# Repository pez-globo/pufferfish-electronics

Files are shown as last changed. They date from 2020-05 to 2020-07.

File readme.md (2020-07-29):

# pufferfish-electronics

Electronic hardware board layout files for the Pufferfish ventilator.

This folder contains the [KiCad](https://kicad-pcb.org/) design files for the Pufferfish ventilator.

To review the hardware files, start by opening the project file `Pufferfish.pro` with KiCad. From there, schematics, boards, and library parts can be viewed.

`Pufferfish.sch` and `Pufferfish.kicad_pcb` are dummy files, kept to aid in managing project resources (eg. footprint and schematic library settings).

The files `sym-lib-table` and `fp-lib-table` define the paths for local part libraries. 
  * these should point to `/library/symbols/` and `/library/footprints/` for symbols and footprints, respectively. 
  * this only applies to projects containing in this folder and not subfolders below it. 
  * for each design project, its own `sym-lib-table` and `fp-lib-table` files were added pointing to: `${KIPRJMOD}/../../library/symbols/Pufferfish.lib` and `${KIPRJMOD}/../../library/footprints/Pufferfish.pretty, respectively`
  * if this relative linking fails, an alternative way to share these library parts amongst each project is to add them to KiCad's global library path (open any project or schematic or pcb, add the appropriate library directories by going to "Preferences/Manage <Footprint/Symbol> Library", and when prompted choose global).

The file `Pufferfish.kicad_wks` contains the template schematic page layout for this project.

Copyright 2020, the Pez Globo team and the Pufferfish project contributors

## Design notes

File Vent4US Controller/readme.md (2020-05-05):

This folder contains the EasyCAD design files for the Vent4US control board, which was forked from the [Octopi](https://octopi.squarespace.com/) project: https://github.com/ethanjli/octopi-driver-board

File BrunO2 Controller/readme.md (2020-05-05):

This folder contains the [Eagle](https://www.autodesk.com/products/eagle/overview) design files for the [BrunO2](https://sites.brown.edu/bruno2/) Control Board v1, as designed by Marc Powell in April of 2020 at Brown Univeristy.

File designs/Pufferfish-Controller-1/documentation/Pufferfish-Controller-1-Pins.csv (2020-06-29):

Board | Name | MCU Pin Name | Board Net | MCU Pin Function | Type | Domain | Description
control | CN11_56 | PF9 | SENSE_O2_OUT | ADC3_INP2 | ADC | oxygen sensor | oxygen sensor output
control | CN11_55 | PD1 | MOTOR1_UART | UART4_TX | UART | motor driver | universal asynchronous transmitter for configuring a motor driver
control | CN11_3 | PC12 | MOTOR2_UART | UART5_TX | UART | motor driver | universal asynchronous transmitter for configuring a motor driver
control | CN11_11 | PF7 | MOTOR3_UART | UART7_TX | UART | motor driver | universal asynchronous transmitter for configuring a motor driver
control | CN11_61 | PE1 | MOTOR4_UART | UART8_TX | UART | motor driver | universal asynchronous transmitter for configuring a motor driver
control | CN12_17 | PB6 | CPU_UART_TX | USART1_TX | USART | computer | microcontroller and computer communication channel
control | CN12_33 | PA10 | CPU_UART_RX | USART1_RX | USART | computer | microcontroller and computer communication channel
control | CN12_23 | PA8 | CPU_UART_CLK | USART1_CK | USART | computer | microcontroller and computer communication channel
control | CN12_12 | PA12 | CPU_UART_RTS | USART1_RTS | USART | computer | microcontroller and computer communication channel
control | CN12_14 | PA11 | CPU_UART_CTS | USART1_CTS | USART | computer | microcontroller and computer communication channel
control | CN12_11 | PA5 | SPI1_SCL | SPI1_SCK | SPI | pressure sensor | pressure sensor communication channel
control | CN12_13 | PA6 | SPI1_MISO | SPI1_MISO | SPI | pressure sensor | pressure sensor communication channel
control | CN12_15 | PA7 | SPI1_MOSI | SPI1_MOSI | SPI | pressure sensor | pressure sensor communication channel
control | CN11_32 | PA4 | <no connection> | SPI1_NSS | SPI | pressure sensor | pressure sensor communication channel
control | CN11_17 | PA15 | BUZZ1_EN | TIM2_CH1 | PWM | buzzer | pulse width modulated line for driving the buzzer
control | CN11_62 | PE6 | LED1_EN | Digital I/O | DIO | light indicator | digital line for indicating program status via a light emitting diode
control | CN11_64 | PG15 | LED2_EN | Digital I/O | DIO | light indicator | digital line for indicating program status via a light emitting diode
control | CN11_66 | PG10 | LED3_EN | Digital I/O | DIO | light indicator | digital line for indicating program status via a light emitting diode
control | CN12_67 | PG7 | MOTOR1_EN | Digital I/O | DIO | motor driver | digital line for enabling a motor driver
control | CN12_43 | PD12 | MOTOR1_DIR | Digital I/O | DIO | motor driver | digital line for controlling motor direction
control | CN12_45 | PD11 | MOTOR1_STEP | Digital I/O | DIO | motor driver | digital line for controlling motor steps
control | CN12_47 | PE10 | MOTOR2_EN | Digital I/O | DIO | motor driver | digital line for enabling a motor driver
control | CN12_49 | PE12 | MOTOR2_DIR | Digital I/O | DIO | motor driver | digital line for controlling motor direction
control | CN12_51 | PE14 | MOTOR2_STEP | Digital I/O | DIO | motor driver | digital line for controlling motor steps
control | CN12_53 | PE15 | MOTOR3_EN | Digital I/O | DIO | motor driver | digital line for enabling a motor driver
control | CN12_55 | PE13 | MOTOR3_DIR | Digital I/O | DIO | motor driver | digital line for controlling motor direction
control | CN12_57 | PF13 | MOTOR3_STEP | Digital I/O | DIO | motor driver | digital line for controlling motor steps
control | CN12_59 | PF12 | MOTOR4_EN | Digital I/O | DIO | motor driver | digital line for enabling a motor driver
control | CN12_61 | PG14 | MOTOR4_DIR | Digital I/O | DIO | motor driver | digital line for controlling motor direction
control | CN12_65 | PD10 | MOTOR4_STEP | Digital I/O | DIO | motor driver | digital line for controlling motor steps
control | CN12_37 | PA3 | DRIVE1_CH1_EN | TIM2_CH4 | PWM | solenoid driver | digital line for enabling a solenoid driver
control | CN12_31 | PB3 | DRIVE1_CH2_EN | TIM2_CH2 | PWM | solenoid driver | digital line for enabling a solenoid driver
control | CN12_24 | PB1 | DRIVE1_CH3_EN | TIM3_CH4 | PWM | solenoid driver | digital line for enabling a solenoid driver
control | CN12_27 | PB4 | DRIVE1_CH4_EN | TIM3_CH1 | PWM | solenoid driver | digital line for enabling a solenoid driver
control | CN12_29 | PB5 | DRIVE1_CH5_EN | TIM3_CH2 | PWM | solenoid driver | digital line for enabling a solenoid driver
control | CN12_2 | PC8 | DRIVE1_CH6_EN | TIM3_CH3 | PWM | solenoid driver | digital line for enabling a solenoid driver
control | CN11_21 | PB7 | DRIVE1_CH7_EN | TIM4_CH2 | PWM | solenoid driver | digital line for enabling a solenoid driver
control | CN12_46 | PD14 | DRIVE2_CH1_EN | TIM4_CH3 | PWM | solenoid driver | digital line for enabling a solenoid driver
control | CN12_48 | PD15 | DRIVE2_CH2_EN | TIM4_CH4 | PWM | solenoid driver | digital line for enabling a solenoid driver
control | CN11_28 | PA0 | DRIVE2_CH3_EN | TIM5_CH1 | PWM | solenoid driver | digital line for enabling a solenoid driver
control | CN12_4 | PC6 | DRIVE2_CH4_EN | TIM8_CH1 | PWM | solenoid driver | digital line for enabling a solenoid driver
control | CN12_19 | PC7 | DRIVE2_CH5_EN | TIM8_CH2 | PWM | solenoid driver | digital line for enabling a solenoid driver
control | CN12_1 | PC9 | DRIVE2_CH6_EN | TIM8_CH4 | PWM | solenoid driver | digital line for enabling a solenoid driver
control | CN12_26 | PB15 | DRIVE2_CH7_EN | TIM12_CH2 | PWM | solenoid driver | digital line for enabling a solenoid driver
control | CN12_52 | PE9 | SENSE_O2_EN | Digital I/O | DIO | oxygen sensor | digital line for enabling an oxygen sensor
control | CN12_56 | PE11 | PRESS1_EN | Digital I/O | DIO | pressure sensor | digital line for enabling a pressure sensor
control | CN12_58 | PF3 | PRESS2_EN | Digital I/O | DIO | pressure sensor | digital line for enabling a pressure sensor
control | CN12_60 | PF15 | PRESS3_EN | Digital I/O | DIO | pressure sensor | digital line for enabling a pressure sensor
control | CN12_62 | PF11 | PRESS4_EN | Digital I/O | DIO | pressure sensor | digital line for enabling a pressure sensor
control | CN12_64 | PE0 | PRESS5_EN | Digital I/O | DIO | pressure sensor | digital line for enabling a pressure sensor
control | CN12_66 | PG8 | PRESS6_EN | Digital I/O | DIO | pressure sensor | digital line for enabling a pressure sensor
control | CN11_68 | PG13 | PRESSX_EN | Digital I/O | DIO | pressure sensor | digital line for enabling/interrupting a set of I2C pressure sensors
control | CN12_16 | PB12 | <no connection> | I2C2_SMBA | I2C | flow sensor | flow sensor (and oxygen sensor) communication channel
control | CN12_25 | PB10 | I2C1_SCL | I2C2_SCL | I2C | flow sensor | flow sensor and oxygen sensor communication channel
control | CN12_18 | PB11 | I2C1_SDA | I2C2_SDA | I2C | flow sensor | flow sensor and oxygen sensor communication channel
control | CN12_68 | PG5 | I2C1_RESET | Digital I/O | DIO | flow sensor | digital line for resetting I2C multiplexer of flow sensors
control | CN12_3 | PB8 | I2C2_SCL | I2C1_SCL | I2C | pressure sensor | pressure sensor communication channel
control | CN12_5 | PB9 | I2C2_SDA | I2C1_SDA | I2C | pressure sensor | pressure sensor communication channel
control | CN12_70 | PG6 | I2C2_RESET | Digital I/O | DIO | pressure sensor | digital line for resetting I2C multiplexer of pressure sensors
control | CN12_41 | PD13 | I2C3_SDA | I2C4_SDA | I2C | oxygen sensor | oxygen sensor communication channel
control | CN12_50 | PF14 | I2C3_SCL | I2C4_SCL | I2C | oxygen sensor | oxygen sensor communication channel
control | CN12_69 | PG4 | PRESS_VDD_EN | Digital I/O | DIO | pressure sensor | pressure sensor voltage supply enable (allows for software resetting certain pressure sensor devices)
interface | CH7_5 | PB13 | ALARM1_LOW | Digital I/O | DIO | buzzer | set high to turn on low-urgency, regulation-compliant, alarm sound
interface | CH10_2 | PG12 | ALARM1_HIGH | Digital I/O | DIO | buzzer | set high to turn on high-urgency, regulation-compliant, alarm sound
interface | CH11_30 | PA1 | ALARM1_MED | Digital I/O | DIO | buzzer | set high to turn on medium-urgency, regulation-compliant, alarm sound
interface | CN8_6 | PC10 | LEDR_CNTRL | Digital I/O | DIO | light indicator | set high to turn on red LED
interface | CN8_8 | PC11 | LEDB_CNTRL | Digital I/O | DIO | light indicator | set high to turn on blue LED
interface | CN8_10 | PD2 | LEDG_CNTRL | Digital I/O | DIO | light indicator | set high to turn on green LED
interface | CN8_14 | PG2 | SET_ALARM_EN | Digital I/O | DIO | user button | digital push input, high = alarm enabled
interface | CN8_16 | PG3 | SET_LOCK | Digital I/O | DIO | user button | digital push input, high = ventilation lock
interface | CH10_15 | PB2 | SET_PWR_SRC | Digital I/O | DIO | user button | digital rocker input for selecting power source
interface | CH10_25 | PE2 | SET_PWR_ON_OFF | Digital I/O | DIO | user button | digital rocker input for power on/off
interface | CN12_28 | PB14 | ALARM2_CNTRL | TIM12_CH1 | PWM | buzzer | pwm signal that controls piezo buzzer (not regulation compliant)
power | CN11_43 | PD6 | LTC4421-PWR-nDISABLE1 | Digital I/O | DIO | power prioritizer | Channel 1 (primary power source) disable
power | CN11_59 | PG0 | LTC4421-PWR-nCH1 | Digital I/O | DIO | power prioritizer | Indicates if primary power source is currently used as power path
power | CN11_39 | PD4 | LTC4421-PWR-nVALID1 | Digital I/O | DIO | power prioritizer | Indicates valid voltage range for primary power source
power | CN11_45 | PD7 | LTC4421-PWR-nDISABLE2 | Digital I/O | DIO | power prioritizer | Channel 2 (backup battery) disable
power | CN11_51 | PF1 | LTC4421-PWR-nFAULT1 | Digital I/O | DIO | power prioritizer | Fault flag for primary power channel
power | CN11_58 | PG1 | LTC4421-PWR-nCH2 | Digital I/O | DIO | power prioritizer | Indicates if battery backup is currently used as power path
power | CN11_41 | PD5 | LTC4421-PWR-nVALID2 | Digital I/O | DIO | power prioritizer | Indicates valid voltage range for backup power source
power | CN11_53 | PF0 | LTC4421-PWR-nFAULT2 | Digital I/O | DIO | power prioritizer | Fault flag for backup power channel
power | CN11_48 | PE4 | VSYS-5V0-PGOOD | Digital I/O | DIO | regulator | 5V Buck PGOOD flag
power | CN11_47 | PE3 | VSYS-3V3-PGOOD | Digital I/O | DIO | regulator | 3.3V Buck PGOOD flag
power | CN11_52 | PF2 | BAT-CHARGE-EN | Digital I/O | DIO | battery | Enables charging path for SLA backup battery
power | CN11_50 | PE5 | BAT-MEAS-EN | Digital I/O | DIO | battery | Enables analog measurement of backup battery
power | CN11_54 | PF8 | BAT-MEAS-ANALOG | ADC3_INP7 | ADC | battery | Analog divider measurement from battery
control | CN12_6 | PC5 | GPIO1 | Digital I/O | DIO | unused | unused general purpose I/O line for off board routing
control | CN12_34 | PC4 | GPIO2 | Digital I/O | DIO | unused | unused general purpose I/O line for off board routing
control | CN12_40 | PE8 | GPIO3 | Digital I/O | DIO | unused | unused general purpose I/O line for off board routing
control | CN12_44 | PE7 | SET_EXTRA | Digital I/O | DIO | unused | unused general purpose I/O line for off board routing

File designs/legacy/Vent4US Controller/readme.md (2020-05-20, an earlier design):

This folder contains the [EasyEDA](https://easyeda.com/) design files for the Vent4US control board, which was forked from the [Octopi](https://octopi.squarespace.com/) project: https://github.com/ethanjli/octopi-driver-board

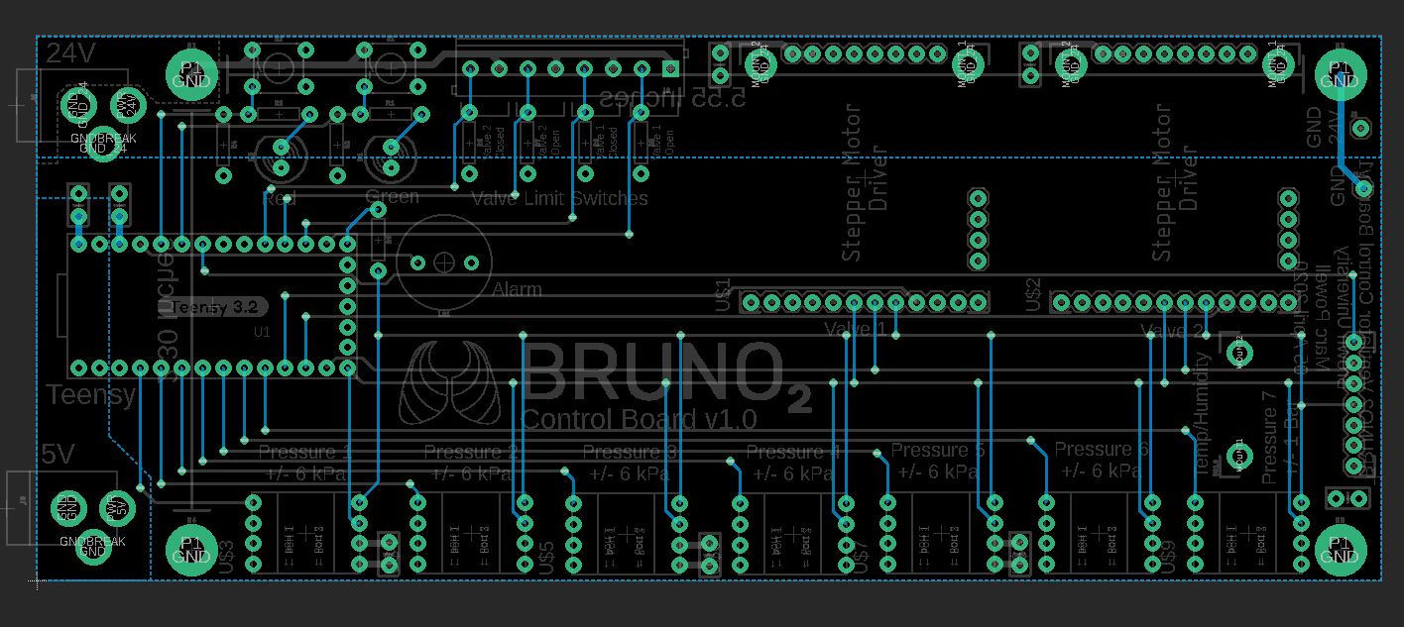
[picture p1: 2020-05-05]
BrunO2 Controller/graphics/Board_Bottom.PNG

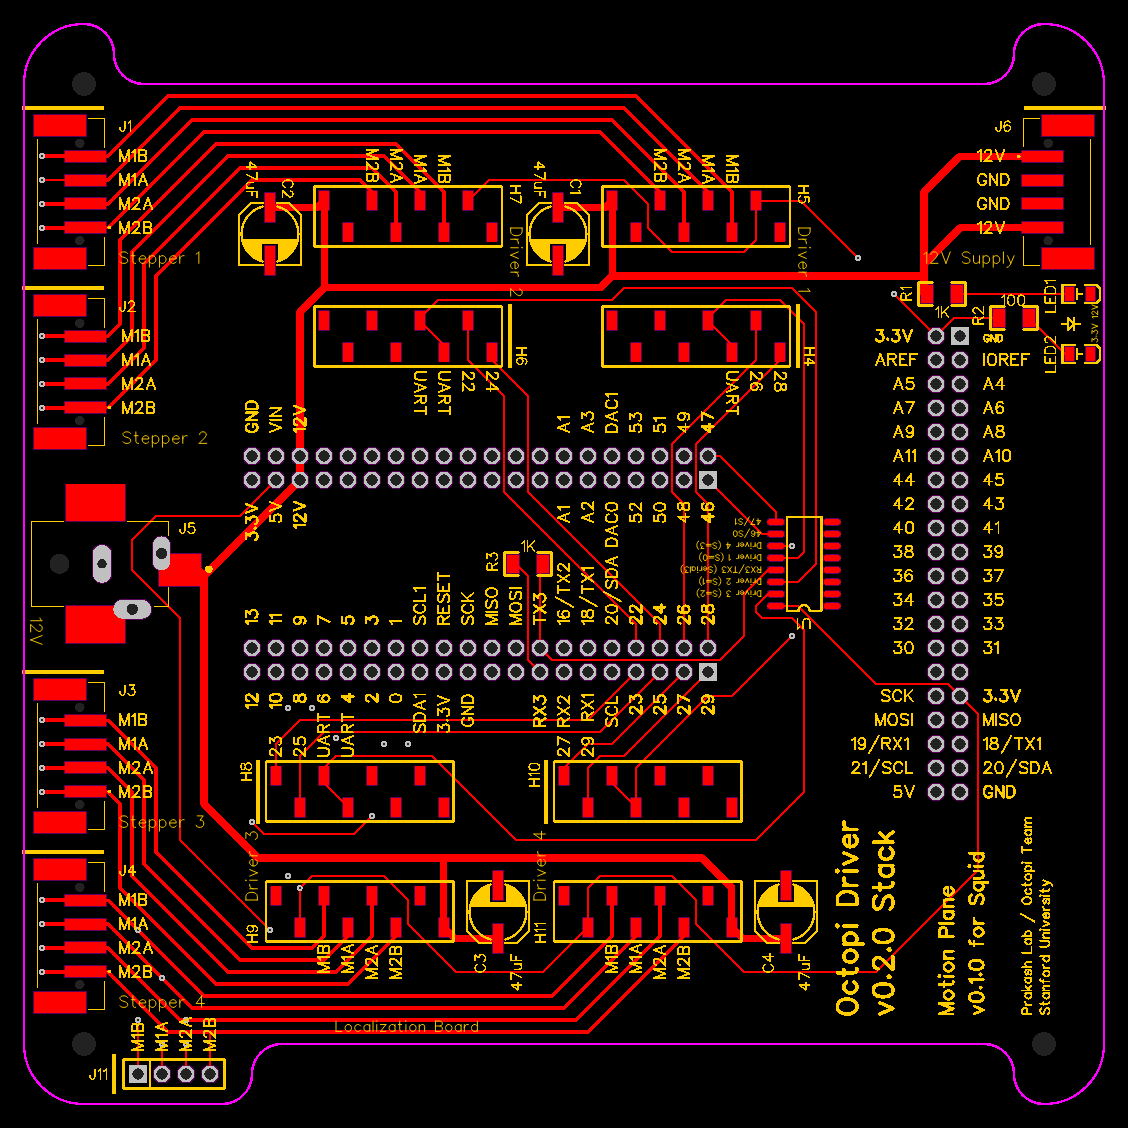
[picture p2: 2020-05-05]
Vent4US Controller/graphics/Layout Top.png

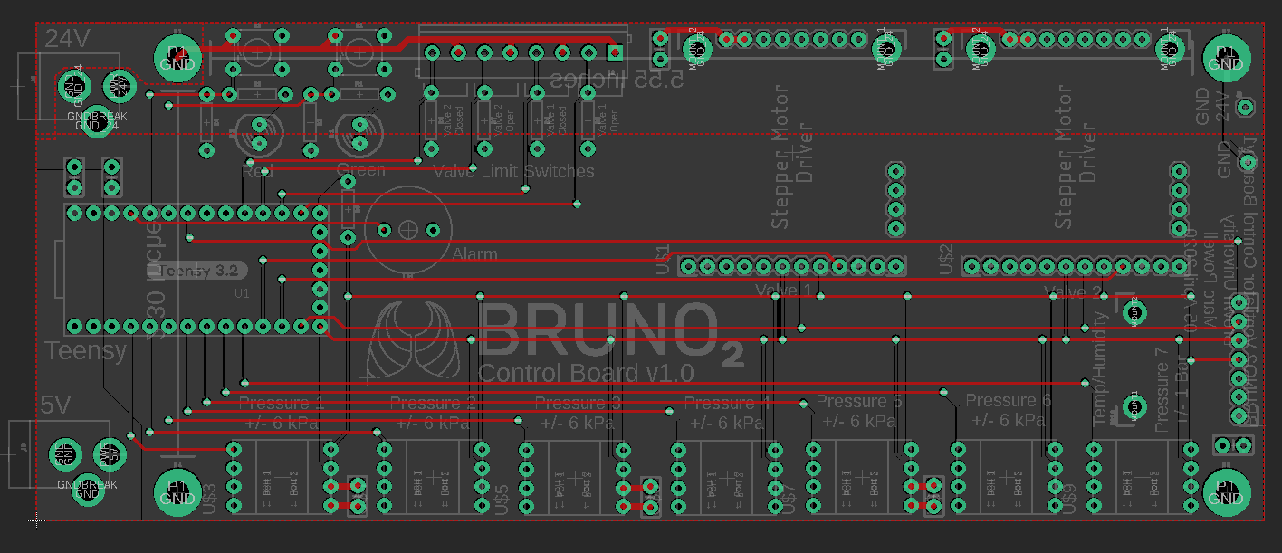
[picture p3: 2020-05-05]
BrunO2 Controller/graphics/Board_Top.PNG

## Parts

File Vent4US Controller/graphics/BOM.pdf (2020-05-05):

BOM for ODS-MPSv0.1.0 | Components

ID

Component

ID | Image Component Name | Mounting Type Manufacturer | Manufacturer Part # | Manufacturer Link | Supplier
Supplier Part # | Supplier Link Supplier Description
ShenZhen OPL MPN Component Notes | Quantity
EasyEDA BOM ID | Designator Notes
1 | 15 | Motion Plane v0.1.0 | Fastener | Seeed Studio

Octopi Team

ODS- MPSv0.1.0 https://github.com/ethanjli/octopi-driver-board/tree/ODS-MPSv0.1.0/Stacked/Motion%20Plane%20for%20Squid Motion Plane v0.1.0 for Squid | 1 N/A
2 | 5
2x20 Female Header, Tall Stacking | PTH

Sullins Connector Solutions

PPPC202LFH
N-M53 RC | https://media.digikey.com/pdf/Data%20Sheets/Sullins%20PDFs/Female_Headers.100_DS.pdf Pololu | 2749 https://www.pololu.com/product/2749
Stackable 0.100″ Female Header with Extra 0.3″ Spacer: 2x20-Pin, Straight | Next version will replace with SMT headers. | 3 | 6 C1,C3,C2

The female side should be on the underside of the board, while the male pins should stick up.

3 | 16
SilentStepStick Stepper Driver Board | Daughter Board Trinamic | TMC2209 | https://www.trinamic.com/support/eval-kits/details/silentstepstick/ Digi-Key
1460-1395- ND | https://www.digikey.com/product-detail/en/trinamic-motion-control-gmbh/TMC2209-SILENTSTEPSTICK/1460-1395-ND/10232488 TMC2209 STEPPER DRIVER BOARD | 4 N/A

Driver 1, Driver 2, Driver 3, Driver 4
Solder the UART/PDN jumper pads on the board first! Then place on the male headers (short ends), confirm correct orientation, and solder.
4 | 17 | 1x8 Female Header | SMT

Sullins Connector Solutions

NPPC081KFX C-RC | https://www.sullinscorp.com/product/?pn=NPPC081KFXC-RC&toggle=in Digi-Key | S5639-ND https://www.digikey.com/product-detail/en/sullins-connector-solutions/NPPC081KFXC-RC/S5639-ND/776098 CONN HDR 8POS 0.1 GOLD SMD | 8 | 8

H4, H5, H6, H7, H8, H9, H10, H11

5 | 9 | 1X8 Male Header | PTH | Pololu | 965 https://www.pololu.com/product/965 Pololu | 965 https://www.pololu.com/product/965 0.100" (2.54 mm) Breakaway Male Header: 1×40-Pin, Straight, Black
Next version will replace with SMT header. Need to break off appropriate length of header. | 8 N/A

H4, H5, H6, H7, H8, H9, H10, H11
Break of appropriate length of header and insert long ends into the female headers.
6 | 18 | 100uF Electrolytic Capacitor | SMT | Nichicon | UCD1E470MC
L1GS | https://www.nichicon.co.jp/english/products/pdfs/e-ucd.pdf (https://www.digikey.com/product-detail/en/nichicon/UCD1E470MCL1GS/493-6385-1-ND/3438899) Digi-Key
| | | | | | 493-6385- 1-ND https://www.digikey.com/product-detail/en/nichicon/UCD1E470MCL1GS/493-6385-1-ND/3438899 CAP ALUM 47UF 20% 25V SMD

UCD1E47
0MCL1GS | 4 | 11
C1,C2,C3, C4 | Confirm correct orientation.
7 | 19 | DC Power Jack | SMT | CUI Devices
PJ-037AH- SMT-TR | https://www.cuidevices.com/product/interconnect/connectors/dc-power-connectors/jacks/pj-037ah-smt-tr Digi-Key

CP- 037AHPJC

T-ND https://www.digikey.com/product-detail/en/cui-devices/PJ-037AH-SMT-TR/CP-037AHPJCT-ND/1530998 CONN PWR JACK 2X5.5MM SOLDER | 1 | 5 J5

Solder the SMT pads first, then solder the PTH pins.

8 | 20 | Green Indicator LED | SMT

Everlight Electronics

17- 21SYGC/S530

-E2/TR8 | http://www.everlight.com/SeriationProduct.aspx?Seq=04c91a6b-2405-e411-8b3b-0002a54e500f (https://www.digikey.com/product-detail/en/everlight-electronics-co-ltd/17-21SYGC-S530-E2-TR8/1080-1500-1-ND/7707772) Digi-Key

1080-1500- 1-ND https://www.digikey.com/product-detail/en/everlight-electronics-co-ltd/17-21SYGC-S530-E2-TR8/1080-1500-1-ND/7707772 LED YELLOW/GREEN CLEAR 0805 SMD

17- 21SYGC/S

530- E2/TR8 | 2 | 12 LED1,LED2 Confirm correct orientation.
9 | 21 | 1K Resistor | SMT | Yageo
RC1206FR- 071KL | https://www.yageo.com/en/Product/Index/rchip/thick_film_general_purpose Digi-Key
311-1.00 KFRCT-ND https://www.digikey.com/product-detail/en/%E5%9E%88-%C3%A1/RC1206FR-071KL/311-1-00KFRCT-ND/731334 RES SMD 1K OHM 1% 1/4W 1206

RC1206JR
-071KL | 2 | 9 R1,R3
10 | 22 | 100 Resistor | SMT | Yageo
RC1206FR- 07100RL | https://www.yageo.com/en/Product/Index/rchip/thick_film_general_purpose Digi-Key
311- 100FRCT- ND | https://www.digikey.com/product-detail/en/%E5%9E%88-%C3%A1/RC1206FR-07100RL/311-100FRCT-ND/731438 RES SMD 100 OHM 1% 1/4W 1206
RC1206JR
-07100RL | 1 | 13 R2
11 | 23 | SP4T Mux/Demux | SMT | Nexperia
74HC4052D, 653 | https://www.nexperia.com/products/analog-logic-ics/i-o-expansion-logic/analog-switches/74HC4052D.html Digi-Key
1727-2808- 1-ND | https://www.digikey.com/product-detail/en/nexperia-usa-inc/74HC4052D-653/1727-2808-1-ND/763388 IC MUX/DEMUX DUAL 4X1 16SOIC

74HC4052 D,653

In a future version, we'll try using the MS1/MS2 UART addressing system instead of a UART mux/demux. | 1 | 10 U1 | Confirm correct orientation.
12 | 24
1x4 Spring Clamp Terminal Block | SMT | Phoenix Contact | 1814650 https://www.phoenixcontact.com/online/portal/us/?uri=pxc-oc-itemdetail:pid=1814650&library=usen&pcck=P-11-01-05&tab=1&selectedCategory=ALL Digi-Key
277-10064- 1-ND | https://www.digikey.com/product-detail/en/phoenix-contact/1814650/277-10064-1-ND/4738862 TERM BLOCK 4POS | 4 | 2 J1,J2,J3,J4
First solder the pads on the side, then solder the SMT pins.
13 | 25
1x6 1.5mm Pitch Right-Angle Header | SMT | JST

S6B-ZR- SM4A-TF(LF)

(SN) | http://www.jst-mfg.com/product/detail_e.php?series=287 (https://www.digikey.com/product-detail/en/jst-sales-america-inc/S6B-ZR-SM4A-TF-LF-SN/455-1610-1-ND/858041) Digi-Key
455-1610- 1-ND | https://www.digikey.com/product-detail/en/jst-sales-america-inc/S6B-ZR-SM4A-TF-LF-SN/455-1610-1-ND/858041 CONN HEADER SMD R/A 6POS 1.5MM | 4 | 1

J7,J8,J9,
J10

First solder the pads on the side, then solder the SMT pins.

14 | 28 | 16 Position 1.5mm Pitch Cable Wiring | JST

A06ZR06ZR2
8H305B | http://www.jst-mfg.com/product/pdf/eng/eZR.pdf (https://www.digikey.com/product-detail/en/jst-sales-america-inc/A06ZR06ZR28H305B/455-3043-ND/6009419) Digi-Key
| | | | | | 455-3043- ND | https://www.digikey.com/product-detail/en/jst-sales-america-inc/A06ZR06ZR28H305B/455-3043-ND/6009419 JUMPER 06ZR-8M-P - 06ZR-8M-P 12" | | 3 N/A

On the underside of the board. First solder the pads on the side, then solder the SMT pins.

15 | 26 | 1x4 KK 254 Male Header | PTH | Molex | 22292041 https://www.molex.com/molex/products/part-detail/pcb_headers/0022292041 Digi-Key | WM2746- ND | https://www.digikey.com/product-detail/en/molex/0022292041/WM2746-ND/1130590 CONN HEADER VERT 4POS 2.54MM | SMT equivalent does not exist. | 1 | 4 J11

Solder so that the plastic tab is closer to the outer perimeter of the board.

16 | 27 | 6-Bit Buffer | SMT | Nexperia
74LVC07AD, 118 | https://www.nexperia.com/products/analog-logic-ics/asynchronous-interface-logic/buffers-inverters-drivers/74LVC07AD.html Digi-Key
1727-3089- 1-ND | https://www.digikey.com/product-detail/en/nexperia-usa-inc/74LVC07AD-118/1727-3089-1-ND/946746 IC BUFFER NON-INVERT 5.5V 14SO

74LVC07A D,118

Need to read with INPUT_PULLUP pins. Supply Vcc with the input voltage level (5V), from the connector. | 2 | 3 U2,U3 | Confirm correct orientation.
17 | 12
AMP Mini CT Right-Angle Header, 16 position | SMT | TE Connectivity | 1-292228-6 | https://www.te.com/usa-en/product-1-292228-6.html Master Electronics 1-292228-6 https://www.masterelectronics.com/te-connectivity-amp-brand/12922286-10181019.html CONN HEADER SMD R/A 16POS 1.5MM
This version has no boss, but the 1-292227-6 version has a boss for alignment and is available on Digikey. The next version will add holes for the boss so we can use 1-292228-6. | 1 | 7 J12

On the underside of the board. First solder the pads on the side, then solder the SMT pins.

BOM for ODS-MPSv0.1.0 | Fusion PCBA
Designator | MPN | Quantity Supplier Link

BOM
ID

Component
ID | Image Component Name | Manufacturer

Manufacturer Part #

ShenZhen OPL MPN In OPL?

Ship to Seeed? | Supplier
Supplier Part # | Supplier Description | Mounting Type Notes

LED1,LED2

| 17-21SYGC/S530- E2/TR8 | 2 https://www.digikey.com/product-detail/en/everlight-electronics-co-ltd/17-21SYGC-S530-E2-TR8/1080-1500-1-ND/7707772 8 | 20 | Green Indicator LED | Everlight Electronics

17-
21SYGC/S530
-E2/TR8

17-
21SYGC/S
530- E2/TR8 | Yes | Digi-Key

1080-1500-
1-ND | LED YELLOW/GREEN CLEAR 0805 SMD | SMT | Confirm correct orientation.
R1,R3 | RC1206JR-071KL | 2 https://www.digikey.com/product-detail/en/%E5%9E%88-%C3%A1/RC1206FR-071KL/311-1-00KFRCT-ND/731334 9 | 21 | 1K Resistor | Yageo

RC1206FR-071KL

RC1206JR
-071KL | Yes | Digi-Key
311-1.00 KFRCT-ND RES SMD 1K OHM 1% 1/4W 1206 | SMT

R2

RC1206JR-
07100RL | 1 https://www.digikey.com/product-detail/en/%E5%9E%88-%C3%A1/RC1206FR-07100RL/311-100FRCT-ND/731438 10 | 22 | 100 Resistor | Yageo

RC1206FR-07100RL

RC1206JR
-07100RL Yes | Digi-Key

311-
100FRCT- ND | RES SMD 100 OHM 1% 1/4W 1206 | SMT

C1,C2,C3,C4

UCD1E470MCL1G
S | 4 https://www.digikey.com/product-detail/en/nichicon/UCD1E470MCL1GS/493-6385-1-ND/3438899 6 | 18 | 100uF Electrolytic Capacitor | Nichicon

UCD1E470MC
L1GS

UCD1E47
| 0MCL1GS Yes | | Digi-Key | 493-6385-
1-ND | CAP ALUM 47UF 20% 25V SMD | SMT | Confirm correct orientation.
H4, H5, H6, H7, H8,
H9, H10, H11 | NPPC081KFXC-RC | 8 https://www.digikey.com/product-detail/en/sullins-connector-solutions/NPPC081KFXC-RC/S5639-ND/776098 4 | 17 | 1x8 Female Header

Sullins Connector Solutions

NPPC081KFX C-RC | No | Yes | Digi-Key | S5639-ND CONN HDR 8POS 0.1 GOLD SMD | SMT
U1 | 74HC4052D,653 | 1 https://www.digikey.com/product-detail/en/nexperia-usa-inc/74HC4052D-653/1727-2808-1-ND/763388 11 | 23 | SP4T Mux/Demux | Nexperia

74HC4052D,
653
74HC4052 D,653 | Yes | Digi-Key
1727-2808-
1-ND | IC MUX/DEMUX DUAL 4X1 16SOIC | SMT | Confirm correct orientation.
J1,J2,J3,J4 | 1814650 | 4 https://www.digikey.com/product-detail/en/phoenix-contact/1814650/277-10064-1-ND/4738862 12 | 24
1x4 Spring Clamp Terminal Block | Phoenix Contact | 1814650 | No | Yes | Digi-Key
277-10064-
1-ND | TERM BLOCK 4POS | SMT

First solder the pads on the side, then solder the SMT pins.

U2,U3 | 74LVC07AD,118 | 2 https://www.digikey.com/product-detail/en/nexperia-usa-inc/74LVC07AD-118/1727-3089-1-ND/946746 16 | 27 | 6-Bit Buffer | Nexperia

74LVC07AD,
118
74LVC07A D,118 | Yes | Digi-Key
1727-3089-
1-ND | IC BUFFER NON-INVERT 5.5V 14SO | SMT | Confirm correct orientation.

J7,J8,J9,J10

S6B-ZR-SM4A-TF
(LF)(SN) | 4 https://www.digikey.com/product-detail/en/jst-sales-america-inc/S6B-ZR-SM4A-TF-LF-SN/455-1610-1-ND/858041 13 | 25
1x6 1.5mm Pitch Right-Angle Header | JST

S6B-ZR- SM4A-TF(LF)

(SN) | No | Yes | Digi-Key

455-1610-
1-ND | CONN HEADER SMD R/A 6POS 1.5MM | SMT

First solder the pads on the side, then solder the SMT pins.

BOM for ODS-MPSv0.1.0 | Manual Assembly

### BOM

ID

### Component

ID | Image Component Name | Manufacturer

### Manufacturer

Part # | Supplier

### Supplier

Part # | Supplier Link Supplier Description
ShenZhen OPL MPN Mounting Type Quantity Designator | Notes
1 | 15 | Motion Plane v0.1.0 | Seeed Studio

### Octopi Team

ODS- MPSv0.1.0 https://github.com/ethanjli/octopi-driver-board/tree/ODS-MPSv0.1.0/Stacked/Motion%20Plane%20for%20Squid Motion Plane v0.1.0 for Squid | Fastener | 1
17 | 12

### AMP Mini CT Right-Angle

Header, 16 position | TE Connectivity | 1-292228-6

### Master

Electronics 1-292228-6 https://www.masterelectronics.com/te-connectivity-amp-brand/12922286-10181019.html CONN HEADER SMD R/A 16POS 1.5MM | SMT | 1 J12

### On the underside of the board. First solder the

pads on the side, then solder the SMT pins.

7 | 19 | DC Power Jack | CUI Devices

### PJ-037AH-

SMT-TR | Digi-Key

CP-
| | | | | 037AHPJC
T-ND | https://www.digikey.com/product-detail/en/cui-devices/PJ-037AH-SMT-TR/CP-037AHPJCT-ND/1530998 CONN PWR JACK 2X5.5MM SOLDER | SMT | 1 J5

### Solder the SMT pads first, then solder the PTH

pins.

15 | 26 | 1x4 KK 254 Male Header | Molex | 22292041 Digi-Key
WM2746- ND | https://www.digikey.com/product-detail/en/molex/0022292041/WM2746-ND/1130590 CONN HEADER VERT 4POS 2.54MM | PTH | 1 J11

### Solder so that the plastic tab is closer to the outer

perimeter of the board.
2 | 5 | 2x20 Female Header, Tall Stacking | Sullins Connector Solutions | PPPC202LFH
N-M53 RC | Pololu | 2749 https://www.pololu.com/product/2749
| | | | | Stackable 0.100″ Female Header with Extra
0.3″ Spacer: 2x20-Pin, Straight | PTH | 3 C1,C3,C2

### The female side should be on the underside of

the board, while the male pins should stick up.
5 | 9 | 1X8 Male Header | Pololu | 965 Pololu | 965 https://www.pololu.com/product/965 0.100" (2.54 mm) Breakaway Male Header:
1×40-Pin, Straight, Black | PTH | 8

H4, H5, H6, H7, H8,

### H9, H10, H11

### Break of appropriate length of header and insert

long ends into the female headers.

3 | 16

### SilentStepStick Stepper Driver

Board | Trinamic | TMC2209 | Digi-Key
1460-1395- ND | https://www.digikey.com/product-detail/en/trinamic-motion-control-gmbh/TMC2209-SILENTSTEPSTICK/1460-1395-ND/10232488 TMC2209 STEPPER DRIVER BOARD | Daughter Board | 4

Driver 1,Driver 2,

### Driver 3,Driver 4

### Solder the UART/PDN jumper pads on the board first! Then place on the male headers (short

ends), confirm correct orientation, and solder.

14 | 28 | 16 Position 1.5mm Pitch Cable JST

### A06ZR06ZR2

8H305B | Digi-Key
455-3043- ND | https://www.digikey.com/product-detail/en/jst-sales-america-inc/A06ZR06ZR28H305B/455-3043-ND/6009419 JUMPER 06ZR-8M-P - 06ZR-8M-P 12" | Wiring | 3

### On the underside of the board. First solder the

pads on the side, then solder the SMT pins.

BOM for ODS-MPSv0.1.0 | Columns
Name | Column Number
ID | 1
Component ID | 2
Image | 3
Component Name | 4
Mounting Type | 5
Manufacturer | 6
Manufacturer Part # | 7
Manufacturer Link | 8
Supplier | 9
Supplier Part # | 10
Supplier Link | 11
Supplier Description | 12
ShenZhen OPL MPN | 13
Component Notes | 14
Quantity | 15
EasyEDA BOM ID | 16
Designator | 17
Notes | 18

BOM for ODS-MPSv0.1.0 | Database Connections
| Spreadsheet Key | Test | Connect
Components | 1zAloSpcvtBr9TqI6Yx1EZMmtNOi7asDnlvC0D3OLPuA | ID | ID

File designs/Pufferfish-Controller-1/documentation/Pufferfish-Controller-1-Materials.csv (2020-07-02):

Part Identifier | Part Count per Board | Manufacturer | Manufacturer Part Number | Digikey Part Number | Type | Value | Description | Symbol | Footprint | References
2N7002E | 1 | Vishay Siliconix | 2N7002E-T1-E3 | 2N7002E-T1-E3 | transistor |  | 0.24A Id, 60V Vds, N-Channel MOSFET, SOT-23 | Pufferfish:2N7002E | Pufferfish:SOT-23 | Q1
5103308-3 | 2 | TE Connectivity | 5103308-3 | A33163-ND | header |  | Headers & Wire Housings 16P 2 ROW HEADER LP | Pufferfish:5103308-3 | Pufferfish:SHDR16W66P254_2X8 | CONN23; CONN24
ABPMAND001PG2A3 | 4 | Honeywell | ABPMAND001PG2A3 | 480-6250-ND | pressure sensor | 0-1psi | ABPMAND001PG2A3, Differential Pressure Sensor 1psi 6-Pin SMT | Pufferfish:ABPMAND001PG2A3 | Pufferfish:ABPMANN030PG2A3 | PRESS1; PRESS2; PRESS3; PRESS9
ABPMANN030PG2A3 | 2 | Honeywell | ABPMANN030PG2A3 | 480-6247-ND | pressure sensor | 0-30psi | ABPMANN030PG2A3, Differential Pressure Sensor 30psi 6-Pin SMT | Pufferfish:ABPMANN030PG2A3 | Pufferfish:ABPMANN030PG2A3 | PRESS7; PRESS8
B2B-PH-SM4-TB(LF)(SN) | 14 | JST Sales America Inc. | B2B-PH-SM4-TB(LF)(SN) | 455-1734-1-ND | header |  | Connector Header Surface Mount 2 position 0.079" (2.00mm) | Pufferfish:B2B-PH-SM4-TB(LF)(SN) | Pufferfish:JST_B2B-PH-SM4-TB | CONN5; CONN6; CONN7; CONN8; CONN9; CONN10; CONN11; CONN12; CONN13; CONN14; CONN15; CONN16; CONN17; CONN18
B4B-PH-SM4-TB(LF)(SN) | 8 | JST Sales America Inc. | B4B-PH-SM4-TB(LF)(SN) | 455-1736-1-ND | header |  | Connector Header Surface Mount 4 position 0.079" (2.00mm) | Pufferfish:B4B-PH-SM4-TB(LF)(SN) | Pufferfish:JST_B4B-PH-SM4-TB | CONN1; CONN2; CONN3; CONN4; CONN19; CONN20; CONN21; CONN22
BUZZER-12MM | 1 | CUI Devices | CSQG703BP | 102-1286-ND | buzzer |  | 12mm Buzzer Transducer, Externally Driven Magnetic 3V 90mA 2kHz 85dB @ 3V, 5cm Through Hole PC Pins | Pufferfish:BUZZER-12MM | Pufferfish:BUZZER-12MM | BUZZ1
CAP_POLAR_SMD_0805-10uF | 12 | KEMET | C0805C106K4PACTU | 399-8012-1-ND | capacitor | 10uF | Polarized capacitor, small symbol, 0805, SMD, SMT | Pufferfish:CAP_POLAR_SMD_0805 | Pufferfish:CAP_POLAR_SMD_0805 | C1; C35; C36; C37; C38; C39; C40; C41; C42; C45; C46; C47; C20; C21; C25; C26; C27; C28; C29; C30; C31; C32; C33; C34
CAP_SMD_0603-100nF | 1 | KEMET | C0603C104Z3VACTU | 399-1100-1-ND | capacitor | 100nF | Unpolarized capacitor, small symbol, 0603, SMD, SMT | Pufferfish:CAP_SMD_0603 | Pufferfish:CAP_SMD_0603 | C43
CAP_SMD_0603-1uF | 21 | KEMET | C0603C105K4RACTU | 399-7847-1-ND | capacitor | 1uF | Unpolarized capacitor, small symbol, 0603, SMD, SMT | Pufferfish:CAP_SMD_0603 | Pufferfish:CAP_SMD_0603 | C2; C3; C4; C5; C6; C7; C8; C9; C10; C11; C12; C13; C14; C15; C16; C17; C18; C19; C22; C24; C44
CAP_SMD_0603-DNP | 1 | N/A | N/A | N/A | capacitor | DNP | Unpolarized capacitor, small symbol, 0603, SMD, SMT | Pufferfish:CAP_SMD_0603 | Pufferfish:CAP_SMD_0603 | C23
HSCMRRN060PDSA3 | 3 | Honeywell | HSCMRRN060PDSA3 | HSCMRRN060PDSA3-ND | pressure sensor | ±60psi | Board Mount Pressure Sensors SMT, Dual Rad Barbed Differential, 3.3V | Pufferfish:HSCMRRN060PDSA3 | Pufferfish:PRESSURE_HSC_SOIC-8 | PRESS10; PRESS11; PRESS12
HSCMRRN100MDSA3 | 3 | Honeywell | HSCMRRN100MDSA3 | HSCMRRN100MDSA3-ND | pressure sensor | ±100mbar | Board Mount Pressure Sensors SMT, Dual Rad Barbed Differential, 3.3V | Pufferfish:HSCMRRN100MDSA3 | Pufferfish:PRESSURE_HSC_SOIC-8 | PRESS4; PRESS5; PRESS6
LMP91000SDE | 1 | Texas Instruments | LMP91000SDE/NOPB | LMP91000SDE/NOPBCT-ND | potentiostat |  | Texas Instruments,LMP91000SDE/NOPB,AFE LMP91000SDE/NOPB, Analogue Front End IC, 1-channel Serial-I2C, 14-Pin WSON | Pufferfish:LMP91000SDE | Pufferfish:SON50P400X400X80-15N | IC3
MAXTEC_Max-12c | 1 | Maxtec | MAX-12c | N/A | oxygen sensor |  | Jumper, 3-pole, both open | Pufferfish:MAXTEC_Max-12c | Pufferfish:TERMINAL_PIN_3_2.54mm | SENSOR1
NUCLEO-F429ZI | 1 | STMicroelectronics | NUCLEO-F429ZI | 497-16280-ND | module |  | STM32 Nucleo-144 development board with STM32F429ZIT6 MCU, supports Arduino, ST Zio and Morpho | Pufferfish:NUCLEO-F429ZI | Pufferfish:MODULE_NUCLEO-F429ZI | MOD1
RES_SMD_0603-0X | 2 | Yageo | RC0603JR-070RL | 311-0.0GRCT-ND | resistor | 0X | Resistor, small US symbol, 0603, SMD, SMT | Pufferfish:RES_SMD_0603 | Pufferfish:RES_SMD_0603 | R14; R275
RES_SMD_0603-10kX | 8 | Panasonic Electronic Components | ERJ-3GEYJ103V | P10KGTR-ND | resistor | 10kX | Resistor, small US symbol, 0603, SMD, SMT | Pufferfish:RES_SMD_0603 | Pufferfish:RES_SMD_0603 | R236; R237; R426; R427; R428; R429; R430; R431
RES_SMD_0603-1X | 1 | Yageo | RC0603FR-071RL | 311-1.00HRTR-ND | resistor | 1X | Resistor, small US symbol, 0603, SMD, SMT | Pufferfish:RES_SMD_0603 | Pufferfish:RES_SMD_0603 | R375
RES_SMD_0603-1kX | 43 | Yageo | RC0603JR-071KL | 311-1.0KGRTR-ND | resistor | 1kX | Resistor, small US symbol, 0603, SMD, SMT | Pufferfish:RES_SMD_0603 | Pufferfish:RES_SMD_0603 | R234; R235; R238; R239; R240; R241; R244; R245; R246; R247; R249; R250; R251; R252; R253; R254; R255; R256; R258; R259; R260; R261; R262; R263; R265; R266; R267; R268; R269; R270; R271; R272; R277; R278; R279; R280; R282; R283; R284; R285; R368; R369; R374
RES_SMD_0603-20kX | 2 | Susumu | RR0816P-203-D | RR08P20.0KDCT-ND | resistor | 20kX | Resistor, small US symbol, 0603, SMD, SMT | Pufferfish:RES_SMD_0603 | Pufferfish:RES_SMD_0603 | R274; R281
RES_SMD_0603-DNP | 18 | N/A | N/A | N/A | resistor | DNP | Resistor, small US symbol, 0603, SMD, SMT | Pufferfish:RES_SMD_0603 | Pufferfish:RES_SMD_0603 | R13; R17; R35; R36; R37; R38; R39; R155; R157; R159; R161; R169; R171; R175; R177; R233; R257; R276
SDP810-125PA | 1 | Sensirion | SDP810-125PA | 1649-1073-ND | pressure sensor | ±125Pa | Sensirion SDP810-125PA, Differential Pressure Sensor +125Pa 4-Pin | Pufferfish:SDP810-125PA | Pufferfish:PRESSURE_SDP81x | PRESS13
SENSIRION_EK-P4_JST | 4 | Sensirion | EK-P4 | 1649-1059-ND | pressure sensor | ±500Pa | Pressure Sensor Development Tools Evaluation kit SDP31 | Pufferfish:SENSIRION_EK-P4_JST | Pufferfish:SENSIRION_EK-P_JST | PRESS14; PRESS15; PRESS17; PRESS18
SENSIRION_SFM3000_JST | 1 | Sensirion | SFM3000-200 | SFM3000-200-ND | pressure sensor | 0-1.25mbar | AIR/GAS FLOW SENSOR +/-200 SLM W (SFM3000-200C) | Pufferfish:SENSIRION_SFM3000_JST | Pufferfish:SENSIRION_SFM3000_JST | PRESS16
SHORT_SMD_0603-0X | 331 | Yageo | RC0603JR-070RL | 311-0.0GRTR-ND | resistor | 0X | Shorting resistor, small US symbol, 0603, SMD, SMT | Pufferfish:SHORT_SMD_0603 | Pufferfish:SHORT_SMD_0603 | R1; R2; R3; R4; R5; R6; R7; R8; R9; R10; R11; R12; R15; R16; R18; R19; R20; R21; R22; R23; R24; R25; R26; R27; R28; R29; R30; R31; R32; R33; R34; R40; R41; R42; R43; R44; R45; R46; R47; R48; R49; R50; R51; R52; R54; R55; R56; R57; R58; R59; R60; R61; R62; R63; R64; R65; R66; R67; R68; R69; R70; R71; R72; R73; R74; R75; R76; R77; R78; R79; R80; R81; R82; R83; R84; R85; R86; R87; R88; R89; R90; R91; R92; R93; R94; R95; R96; R97; R98; R99; R100; R101; R102; R103; R104; R105; R106; R107; R108; R109; R110; R111; R112; R113; R114; R115; R116; R117; R118; R119; R120; R121; R122; R123; R124; R125; R126; R127; R128; R129; R130; R131; R132; R133; R134; R135; R136; R137; R138; R139; R140; R141; R142; R143; R144; R145; R146; R147; R148; R149; R150; R151; R152; R153; R154; R156; R158; R160; R162; R163; R164; R165; R166; R167; R168; R170; R172; R173; R174; R176; R178; R179; R180; R181; R182; R183; R184; R185; R186; R187; R188; R189; R190; R191; R192; R193; R194; R195; R196; R197; R198; R199; R200; R201; R202; R203; R204; R205; R206; R207; R208; R209; R210; R211; R212; R213; R214; R215; R216; R217; R218; R219; R220; R221; R222; R223; R224; R225; R226; R227; R228; R229; R230; R231; R232; R242; R243; R248; R264; R273; R286; R287; R288; R289; R290; R291; R292; R293; R294; R295; R296; R297; R298; R299; R302; R303; R304; R305; R306; R307; R308; R309; R310; R311; R312; R313; R314; R315; R324; R325; R326; R327; R328; R329; R330; R331; R332; R333; R334; R335; R336; R337; R338; R339; R340; R341; R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
SHORT_SMD_0805-0X | 30 | Yageo | RC0805JR-070RL | 311-0.0ARTR-ND | resistor | 0X | Shorting resistor, small US symbol, 0603, SMD, SMT | Pufferfish:SHORT_SMD_0805 | Pufferfish:SHORT_SMD_0805 | R53; R300; R301; R316; R317; R318; R319; R320; R321; R322; R323; R370; R371; R372; R373; R376; R377; R384; R385; R396; R397; R403; R404; R405; R412; R413; R420; R421; R422; R423
TCA9548APWR | 2 | Texas Instruments | 296-34905-2-ND | 296-34905-2-ND | multiplexer |  | TEXAS INSTRUMENTS - TCA9548APWR - I2C SWITCH W/ RESET, 8-CH, TSSOP-24 | Pufferfish:TCA9548APWR | Pufferfish:SOP65P640X120-24N | IC1; IC2
TERMINAL_SCREW_4_2.54mm | 3 | On Shore Technology Inc. | OSTVN04A150 | ED10563-ND | header |  | Screw terminal, connector, 4x1 pin, 2.54mm | Pufferfish:TERMINAL_SCREW_4_2.54mm | Pufferfish:TERMINAL_PIN_4_2.54mm | J1; J2; J4
TERMINAL_SCREW_8_2.54mm | 1 | On Shore Technology Inc. | OSTVN08A150 | ED10566-ND | header |  | Screw terminal, connector, 8x1 pin, 2.54mm | Pufferfish:TERMINAL_SCREW_8_2.54mm | Pufferfish:TERMINAL_PIN_8_2.54mm | J3
TMC2209-SilentStepStick | 4 | Trinamic Motion Control | TMC2209 SILENTSTEPSTICK | 1460-1395-ND | module |  | Stepper motor controller & driver | Pufferfish:TMC2209-SilentStepStick | Pufferfish:MODULE_TMC2209_SilentStepStick | DRIVE3; DRIVE4; DRIVE5; DRIVE6
TP0610T | 1 | Microchip Technology | TP0610T-G | TP0610T-GCT-ND | transistor |  | -0.18A Id, -60V Vds, P-Channel MOSFET, SOT-23 | Pufferfish:TP0610T | Pufferfish:SOT-23 | Q2
TPL7407LADR | 2 | Texas Instruments | TPL7407LADR | 296-51862-1-ND | switch array |  | Gate Drivers 30-V, 7-Channel NMOS Array Low-Side Driver 16-SOIC -40 to 125 | Pufferfish:TPL7407LADR | Pufferfish:SOIC127P600X175-16N | DRIVE1; DRIVE2
UCQ1E101MCL1GS-100uF | 6 | Nichicon | UCQ1E101MCL1GS | 493-17814-1-ND | capacitor | 100uF | Aluminum Electrolytic Capacitors - SMD 25V 100uf 20% Audio-SMT | Pufferfish:UCQ1E101MCL1GS | Pufferfish:CAPAE660X820N | C48; C49; C50; C51; C52; C53
W25Q16JVSSIQ | 1 | Winbond Electronics | W25Q16JVSSIQ | W25Q16JVSSIQ-ND | memory |  | NOR Flash spiFlash, 3V, 16M-bit, 4Kb Uniform Sector | Pufferfish:W25Q16JVSSIQ | Pufferfish:SOIC127P790X216-8N | IC4
LED_SMD_0805-red | 1 | Lite-On Inc. | LTST-C171KRKT | 160-1427-1-ND | light emitting diode | red | Light emitting diode, filled shape, SMT, SMD | Pufferfish:LED_SMD_0805 | Pufferfish:LED_SMD_0805 | D1
LED_SMD_0805-green | 1 | Lite-On Inc. | LTST-C171GKT | 160-1423-1-ND | light emitting diode | green | Light emitting diode, filled shape, SMT, SMD | Pufferfish:LED_SMD_0805 | Pufferfish:LED_SMD_0805 | D2
LED_SMD_0805-blue | 1 | Lite-On Inc. | LTST-C171TBKT | 160-1645-1-ND | light emitting diode | blue | Light emitting diode, filled shape, SMT, SMD | Pufferfish:LED_SMD_0805 | Pufferfish:LED_SMD_0805 | D3
STANDOFF_ELECTRICAL | 6 | Keystone Electronics | 1902F | 36-1902F-ND | standoff |  | Standoff for #4 phillips button head screw (3mm hole diameter, with optional electrical connection) (0.125 inch / 3.175 mm diameter hole) [Hex Standoff Threaded #4-40 Nylon 0.625" (15.88mm) 5/8" Natural] [screw thread: #4-40, length: 0.625" / 15.88mm] | Pufferfish:STANDOFF_ELECTRICAL | Pufferfish:STANDOFF-ELECTRICAL-NOTHERMALS | H1; H2; H3; H4; H5; H6
STANDOFF_ELECTRICAL_SCREW | 6 | B&F Fastener Supply | NY PMS 440 0025 PH | H542-ND | standoff |  | #4 phillips button head screw | Pufferfish:STANDOFF_ELECTRICAL | Pufferfish:STANDOFF-ELECTRICAL-NOTHERMALS | H1; H2; H3; H4; H5; H6

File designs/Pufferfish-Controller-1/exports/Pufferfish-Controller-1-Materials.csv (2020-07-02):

Source: | /Users/chrisarcadia/Dropbox (Brown)/Ventilator/repositories/pufferfish-electronics/designs/Pufferfish-Controller-1/Pufferfish-Controller-1.sch
Date: | Thursday, July 02, 2020 at 11:10:22 AM
Tool: | Eeschema (5.1.5-0-10_14)
Component Count: | 559
Ref | Value | Part | Footprint | Description | Vendor | Manufacturer | Datasheet | Tolerance | Resistance | Capacitance | Pressure
BUZZ1 | BUZZER-12MM | Pufferfish:BUZZER-12MM | Pufferfish:BUZZER-12MM | Generic 12mm Buzzer
C1 | CAP_POLAR_SMD_0805 | Pufferfish:CAP_POLAR_SMD_0805 | Pufferfish:CAP_POLAR_SMD_0805 | Polarized capacitor, small symbol, 0805, SMD, SMT |  |  | ~ | ?% |  | 47uF
C2 | CAP_SMD_0603 | Pufferfish:CAP_SMD_0603 | Pufferfish:CAP_SMD_0603 | Unpolarized capacitor, small symbol, 0603, SMD, SMT |  |  | ~ | ?% |  | 1uF
C3 | CAP_SMD_0603 | Pufferfish:CAP_SMD_0603 | Pufferfish:CAP_SMD_0603 | Unpolarized capacitor, small symbol, 0603, SMD, SMT |  |  | ~ | ?% |  | 1uF
C4 | CAP_SMD_0603 | Pufferfish:CAP_SMD_0603 | Pufferfish:CAP_SMD_0603 | Unpolarized capacitor, small symbol, 0603, SMD, SMT |  |  | ~ | ?% |  | 1uF
C5 | CAP_SMD_0603 | Pufferfish:CAP_SMD_0603 | Pufferfish:CAP_SMD_0603 | Unpolarized capacitor, small symbol, 0603, SMD, SMT |  |  | ~ | ?% |  | 1uF
C6 | CAP_SMD_0603 | Pufferfish:CAP_SMD_0603 | Pufferfish:CAP_SMD_0603 | Unpolarized capacitor, small symbol, 0603, SMD, SMT |  |  | ~ | ?% |  | 1uF
C7 | CAP_SMD_0603 | Pufferfish:CAP_SMD_0603 | Pufferfish:CAP_SMD_0603 | Unpolarized capacitor, small symbol, 0603, SMD, SMT |  |  | ~ | ?% |  | 1uF
C8 | CAP_SMD_0603 | Pufferfish:CAP_SMD_0603 | Pufferfish:CAP_SMD_0603 | Unpolarized capacitor, small symbol, 0603, SMD, SMT |  |  | ~ | ?% |  | 1uF
C9 | CAP_SMD_0603 | Pufferfish:CAP_SMD_0603 | Pufferfish:CAP_SMD_0603 | Unpolarized capacitor, small symbol, 0603, SMD, SMT |  |  | ~ | ?% |  | 1uF
C10 | CAP_SMD_0603 | Pufferfish:CAP_SMD_0603 | Pufferfish:CAP_SMD_0603 | Unpolarized capacitor, small symbol, 0603, SMD, SMT |  |  | ~ | ?% |  | 1uF
C11 | CAP_SMD_0603 | Pufferfish:CAP_SMD_0603 | Pufferfish:CAP_SMD_0603 | Unpolarized capacitor, small symbol, 0603, SMD, SMT |  |  | ~ | ?% |  | 1uF
C12 | CAP_SMD_0603 | Pufferfish:CAP_SMD_0603 | Pufferfish:CAP_SMD_0603 | Unpolarized capacitor, small symbol, 0603, SMD, SMT |  |  | ~ | ?% |  | 1uF
C13 | CAP_SMD_0603 | Pufferfish:CAP_SMD_0603 | Pufferfish:CAP_SMD_0603 | Unpolarized capacitor, small symbol, 0603, SMD, SMT |  |  | ~ | ?% |  | 1uF
C14 | CAP_SMD_0603 | Pufferfish:CAP_SMD_0603 | Pufferfish:CAP_SMD_0603 | Unpolarized capacitor, small symbol, 0603, SMD, SMT |  |  | ~ | ?% |  | 1uF
C15 | CAP_SMD_0603 | Pufferfish:CAP_SMD_0603 | Pufferfish:CAP_SMD_0603 | Unpolarized capacitor, small symbol, 0603, SMD, SMT |  |  | ~ | ?% |  | 1uF
C16 | CAP_SMD_0603 | Pufferfish:CAP_SMD_0603 | Pufferfish:CAP_SMD_0603 | Unpolarized capacitor, small symbol, 0603, SMD, SMT |  |  | ~ | ?% |  | 1uF
C17 | CAP_SMD_0603 | Pufferfish:CAP_SMD_0603 | Pufferfish:CAP_SMD_0603 | Unpolarized capacitor, small symbol, 0603, SMD, SMT |  |  | ~ | ?% |  | 1uF
C18 | CAP_SMD_0603 | Pufferfish:CAP_SMD_0603 | Pufferfish:CAP_SMD_0603 | Unpolarized capacitor, small symbol, 0603, SMD, SMT |  |  | ~ | ?% |  | 1uF
C19 | CAP_SMD_0603 | Pufferfish:CAP_SMD_0603 | Pufferfish:CAP_SMD_0603 | Unpolarized capacitor, small symbol, 0603, SMD, SMT |  |  | ~ | ?% |  | 1uF
C20 | CAP_POLAR_SMD_0805 | Pufferfish:CAP_POLAR_SMD_0805 | Pufferfish:CAP_POLAR_SMD_0805 | Polarized capacitor, small symbol, 0805, SMD, SMT |  |  | ~ | ?% |  | 10uF
C21 | CAP_POLAR_SMD_0805 | Pufferfish:CAP_POLAR_SMD_0805 | Pufferfish:CAP_POLAR_SMD_0805 | Polarized capacitor, small symbol, 0805, SMD, SMT |  |  | ~ | ?% |  | 10uF
C22 | CAP_SMD_0603 | Pufferfish:CAP_SMD_0603 | Pufferfish:CAP_SMD_0603 | Unpolarized capacitor, small symbol, 0603, SMD, SMT |  |  | ~ | ?% |  | 1uF
C23 | CAP_SMD_0603 | Pufferfish:CAP_SMD_0603 | Pufferfish:CAP_SMD_0603 | Unpolarized capacitor, small symbol, 0603, SMD, SMT |  |  | ~ | ?% |  | DNP
C24 | CAP_SMD_0603 | Pufferfish:CAP_SMD_0603 | Pufferfish:CAP_SMD_0603 | Unpolarized capacitor, small symbol, 0603, SMD, SMT |  |  | ~ | ?% |  | 1uF
C25 | CAP_POLAR_SMD_0805 | Pufferfish:CAP_POLAR_SMD_0805 | Pufferfish:CAP_POLAR_SMD_0805 | Polarized capacitor, small symbol, 0805, SMD, SMT |  |  | ~ | ?% |  | 10uF
C26 | CAP_POLAR_SMD_0805 | Pufferfish:CAP_POLAR_SMD_0805 | Pufferfish:CAP_POLAR_SMD_0805 | Polarized capacitor, small symbol, 0805, SMD, SMT |  |  | ~ | ?% |  | 10uF
C27 | CAP_POLAR_SMD_0805 | Pufferfish:CAP_POLAR_SMD_0805 | Pufferfish:CAP_POLAR_SMD_0805 | Polarized capacitor, small symbol, 0805, SMD, SMT |  |  | ~ | ?% |  | 10uF
C28 | CAP_POLAR_SMD_0805 | Pufferfish:CAP_POLAR_SMD_0805 | Pufferfish:CAP_POLAR_SMD_0805 | Polarized capacitor, small symbol, 0805, SMD, SMT |  |  | ~ | ?% |  | 10uF
C29 | CAP_POLAR_SMD_0805 | Pufferfish:CAP_POLAR_SMD_0805 | Pufferfish:CAP_POLAR_SMD_0805 | Polarized capacitor, small symbol, 0805, SMD, SMT |  |  | ~ | ?% |  | 10uF
C30 | CAP_POLAR_SMD_0805 | Pufferfish:CAP_POLAR_SMD_0805 | Pufferfish:CAP_POLAR_SMD_0805 | Polarized capacitor, small symbol, 0805, SMD, SMT |  |  | ~ | ?% |  | 10uF
C31 | CAP_POLAR_SMD_0805 | Pufferfish:CAP_POLAR_SMD_0805 | Pufferfish:CAP_POLAR_SMD_0805 | Polarized capacitor, small symbol, 0805, SMD, SMT |  |  | ~ | ?% |  | 10uF
C32 | CAP_POLAR_SMD_0805 | Pufferfish:CAP_POLAR_SMD_0805 | Pufferfish:CAP_POLAR_SMD_0805 | Polarized capacitor, small symbol, 0805, SMD, SMT |  |  | ~ | ?% |  | 10uF
C33 | CAP_POLAR_SMD_0805 | Pufferfish:CAP_POLAR_SMD_0805 | Pufferfish:CAP_POLAR_SMD_0805 | Polarized capacitor, small symbol, 0805, SMD, SMT |  |  | ~ | ?% |  | 10uF
C34 | CAP_POLAR_SMD_0805 | Pufferfish:CAP_POLAR_SMD_0805 | Pufferfish:CAP_POLAR_SMD_0805 | Polarized capacitor, small symbol, 0805, SMD, SMT |  |  | ~ | ?% |  | 10uF
C35 | CAP_POLAR_SMD_0805 | Pufferfish:CAP_POLAR_SMD_0805 | Pufferfish:CAP_POLAR_SMD_0805 | Polarized capacitor, small symbol, 0805, SMD, SMT |  |  | ~ | ?% |  | 47uF
C36 | CAP_POLAR_SMD_0805 | Pufferfish:CAP_POLAR_SMD_0805 | Pufferfish:CAP_POLAR_SMD_0805 | Polarized capacitor, small symbol, 0805, SMD, SMT |  |  | ~ | ?% |  | 47uF
C37 | CAP_POLAR_SMD_0805 | Pufferfish:CAP_POLAR_SMD_0805 | Pufferfish:CAP_POLAR_SMD_0805 | Polarized capacitor, small symbol, 0805, SMD, SMT |  |  | ~ | ?% |  | 47uF
C38 | CAP_POLAR_SMD_0805 | Pufferfish:CAP_POLAR_SMD_0805 | Pufferfish:CAP_POLAR_SMD_0805 | Polarized capacitor, small symbol, 0805, SMD, SMT |  |  | ~ | ?% |  | 47uF
C39 | CAP_POLAR_SMD_0805 | Pufferfish:CAP_POLAR_SMD_0805 | Pufferfish:CAP_POLAR_SMD_0805 | Polarized capacitor, small symbol, 0805, SMD, SMT |  |  | ~ | ?% |  | 47uF
C40 | CAP_POLAR_SMD_0805 | Pufferfish:CAP_POLAR_SMD_0805 | Pufferfish:CAP_POLAR_SMD_0805 | Polarized capacitor, small symbol, 0805, SMD, SMT |  |  | ~ | ?% |  | 47uF
C41 | CAP_POLAR_SMD_0805 | Pufferfish:CAP_POLAR_SMD_0805 | Pufferfish:CAP_POLAR_SMD_0805 | Polarized capacitor, small symbol, 0805, SMD, SMT |  |  | ~ | ?% |  | 47uF
C42 | CAP_POLAR_SMD_0805 | Pufferfish:CAP_POLAR_SMD_0805 | Pufferfish:CAP_POLAR_SMD_0805 | Polarized capacitor, small symbol, 0805, SMD, SMT |  |  | ~ | ?% |  | 47uF
C43 | CAP_SMD_0603 | Pufferfish:CAP_SMD_0603 | Pufferfish:CAP_SMD_0603 | Unpolarized capacitor, small symbol, 0603, SMD, SMT |  |  | ~ | ?% |  | 100nF
C44 | CAP_SMD_0603 | Pufferfish:CAP_SMD_0603 | Pufferfish:CAP_SMD_0603 | Unpolarized capacitor, small symbol, 0603, SMD, SMT |  |  | ~ | ?% |  | 1uF
C45 | CAP_POLAR_SMD_0805 | Pufferfish:CAP_POLAR_SMD_0805 | Pufferfish:CAP_POLAR_SMD_0805 | Polarized capacitor, small symbol, 0805, SMD, SMT |  |  | ~ | ?% |  | 47uF
C46 | CAP_POLAR_SMD_0805 | Pufferfish:CAP_POLAR_SMD_0805 | Pufferfish:CAP_POLAR_SMD_0805 | Polarized capacitor, small symbol, 0805, SMD, SMT |  |  | ~ | ?% |  | 47uF
C47 | CAP_POLAR_SMD_0805 | Pufferfish:CAP_POLAR_SMD_0805 | Pufferfish:CAP_POLAR_SMD_0805 | Polarized capacitor, small symbol, 0805, SMD, SMT |  |  | ~ | ?% |  | 47uF
C48 | UCQ1E101MCL1GS | Pufferfish:UCQ1E101MCL1GS | Pufferfish:CAPAE660X820N | Aluminum Electrolytic Capacitors - SMD 25V 100uf 20% Audio-SMT |  |  | https://componentsearchengine.com/Datasheets/1/UCQ1E101MCL1GS.pdf | 20% |  | 100uF
C49 | UCQ1E101MCL1GS | Pufferfish:UCQ1E101MCL1GS | Pufferfish:CAPAE660X820N | Aluminum Electrolytic Capacitors - SMD 25V 100uf 20% Audio-SMT |  |  | https://componentsearchengine.com/Datasheets/1/UCQ1E101MCL1GS.pdf | 20% |  | 100uF
C50 | UCQ1E101MCL1GS | Pufferfish:UCQ1E101MCL1GS | Pufferfish:CAPAE660X820N | Aluminum Electrolytic Capacitors - SMD 25V 100uf 20% Audio-SMT |  |  | https://componentsearchengine.com/Datasheets/1/UCQ1E101MCL1GS.pdf | 20% |  | 100uF
C51 | UCQ1E101MCL1GS | Pufferfish:UCQ1E101MCL1GS | Pufferfish:CAPAE660X820N | Aluminum Electrolytic Capacitors - SMD 25V 100uf 20% Audio-SMT |  |  | https://componentsearchengine.com/Datasheets/1/UCQ1E101MCL1GS.pdf | 20% |  | 100uF
C52 | UCQ1E101MCL1GS | Pufferfish:UCQ1E101MCL1GS | Pufferfish:CAPAE660X820N | Aluminum Electrolytic Capacitors - SMD 25V 100uf 20% Audio-SMT |  |  | https://componentsearchengine.com/Datasheets/1/UCQ1E101MCL1GS.pdf | 20% |  | 100uF
C53 | UCQ1E101MCL1GS | Pufferfish:UCQ1E101MCL1GS | Pufferfish:CAPAE660X820N | Aluminum Electrolytic Capacitors - SMD 25V 100uf 20% Audio-SMT |  |  | https://componentsearchengine.com/Datasheets/1/UCQ1E101MCL1GS.pdf | 20% |  | 100uF
CONN1 | B4B-PH-SM4-TB(LF)(SN) | Pufferfish:B4B-PH-SM4-TB(LF)(SN) | Pufferfish:JST_B4B-PH-SM4-TB | Connector Header Surface Mount 4 position 0.079" (2.00mm) |  | JST Sales America Inc. | JST
CONN2 | B4B-PH-SM4-TB(LF)(SN) | Pufferfish:B4B-PH-SM4-TB(LF)(SN) | Pufferfish:JST_B4B-PH-SM4-TB | Connector Header Surface Mount 4 position 0.079" (2.00mm) |  | JST Sales America Inc. | JST
CONN3 | B4B-PH-SM4-TB(LF)(SN) | Pufferfish:B4B-PH-SM4-TB(LF)(SN) | Pufferfish:JST_B4B-PH-SM4-TB | Connector Header Surface Mount 4 position 0.079" (2.00mm) |  | JST Sales America Inc. | JST
CONN4 | B4B-PH-SM4-TB(LF)(SN) | Pufferfish:B4B-PH-SM4-TB(LF)(SN) | Pufferfish:JST_B4B-PH-SM4-TB | Connector Header Surface Mount 4 position 0.079" (2.00mm) |  | JST Sales America Inc. | JST
CONN5 | B2B-PH-SM4-TB(LF)(SN) | Pufferfish:B2B-PH-SM4-TB(LF)(SN) | Pufferfish:JST_B2B-PH-SM4-TB | Connector Header Surface Mount 2 position 0.079" (2.00mm) |  | JST Sales America Inc. | http://www.jst-mfg.com/product/pdf/eng/ePH.pdf
CONN6 | B2B-PH-SM4-TB(LF)(SN) | Pufferfish:B2B-PH-SM4-TB(LF)(SN) | Pufferfish:JST_B2B-PH-SM4-TB | Connector Header Surface Mount 2 position 0.079" (2.00mm) |  | JST Sales America Inc. | http://www.jst-mfg.com/product/pdf/eng/ePH.pdf
CONN7 | B2B-PH-SM4-TB(LF)(SN) | Pufferfish:B2B-PH-SM4-TB(LF)(SN) | Pufferfish:JST_B2B-PH-SM4-TB | Connector Header Surface Mount 2 position 0.079" (2.00mm) |  | JST Sales America Inc. | http://www.jst-mfg.com/product/pdf/eng/ePH.pdf
CONN8 | B2B-PH-SM4-TB(LF)(SN) | Pufferfish:B2B-PH-SM4-TB(LF)(SN) | Pufferfish:JST_B2B-PH-SM4-TB | Connector Header Surface Mount 2 position 0.079" (2.00mm) |  | JST Sales America Inc. | http://www.jst-mfg.com/product/pdf/eng/ePH.pdf
CONN9 | B2B-PH-SM4-TB(LF)(SN) | Pufferfish:B2B-PH-SM4-TB(LF)(SN) | Pufferfish:JST_B2B-PH-SM4-TB | Connector Header Surface Mount 2 position 0.079" (2.00mm) |  | JST Sales America Inc. | http://www.jst-mfg.com/product/pdf/eng/ePH.pdf
CONN10 | B2B-PH-SM4-TB(LF)(SN) | Pufferfish:B2B-PH-SM4-TB(LF)(SN) | Pufferfish:JST_B2B-PH-SM4-TB | Connector Header Surface Mount 2 position 0.079" (2.00mm) |  | JST Sales America Inc. | http://www.jst-mfg.com/product/pdf/eng/ePH.pdf
CONN11 | B2B-PH-SM4-TB(LF)(SN) | Pufferfish:B2B-PH-SM4-TB(LF)(SN) | Pufferfish:JST_B2B-PH-SM4-TB | Connector Header Surface Mount 2 position 0.079" (2.00mm) |  | JST Sales America Inc. | http://www.jst-mfg.com/product/pdf/eng/ePH.pdf
CONN12 | B2B-PH-SM4-TB(LF)(SN) | Pufferfish:B2B-PH-SM4-TB(LF)(SN) | Pufferfish:JST_B2B-PH-SM4-TB | Connector Header Surface Mount 2 position 0.079" (2.00mm) |  | JST Sales America Inc. | http://www.jst-mfg.com/product/pdf/eng/ePH.pdf
CONN13 | B2B-PH-SM4-TB(LF)(SN) | Pufferfish:B2B-PH-SM4-TB(LF)(SN) | Pufferfish:JST_B2B-PH-SM4-TB | Connector Header Surface Mount 2 position 0.079" (2.00mm) |  | JST Sales America Inc. | http://www.jst-mfg.com/product/pdf/eng/ePH.pdf
CONN14 | B2B-PH-SM4-TB(LF)(SN) | Pufferfish:B2B-PH-SM4-TB(LF)(SN) | Pufferfish:JST_B2B-PH-SM4-TB | Connector Header Surface Mount 2 position 0.079" (2.00mm) |  | JST Sales America Inc. | http://www.jst-mfg.com/product/pdf/eng/ePH.pdf
CONN15 | B2B-PH-SM4-TB(LF)(SN) | Pufferfish:B2B-PH-SM4-TB(LF)(SN) | Pufferfish:JST_B2B-PH-SM4-TB | Connector Header Surface Mount 2 position 0.079" (2.00mm) |  | JST Sales America Inc. | http://www.jst-mfg.com/product/pdf/eng/ePH.pdf
CONN16 | B2B-PH-SM4-TB(LF)(SN) | Pufferfish:B2B-PH-SM4-TB(LF)(SN) | Pufferfish:JST_B2B-PH-SM4-TB | Connector Header Surface Mount 2 position 0.079" (2.00mm) |  | JST Sales America Inc. | http://www.jst-mfg.com/product/pdf/eng/ePH.pdf
CONN17 | B2B-PH-SM4-TB(LF)(SN) | Pufferfish:B2B-PH-SM4-TB(LF)(SN) | Pufferfish:JST_B2B-PH-SM4-TB | Connector Header Surface Mount 2 position 0.079" (2.00mm) |  | JST Sales America Inc. | http://www.jst-mfg.com/product/pdf/eng/ePH.pdf
CONN18 | B2B-PH-SM4-TB(LF)(SN) | Pufferfish:B2B-PH-SM4-TB(LF)(SN) | Pufferfish:JST_B2B-PH-SM4-TB | Connector Header Surface Mount 2 position 0.079" (2.00mm) |  | JST Sales America Inc. | http://www.jst-mfg.com/product/pdf/eng/ePH.pdf
CONN19 | B4B-PH-SM4-TB(LF)(SN) | Pufferfish:B4B-PH-SM4-TB(LF)(SN) | Pufferfish:JST_B4B-PH-SM4-TB | Connector Header Surface Mount 4 position 0.079" (2.00mm) |  | JST Sales America Inc. | JST
CONN20 | B4B-PH-SM4-TB(LF)(SN) | Pufferfish:B4B-PH-SM4-TB(LF)(SN) | Pufferfish:JST_B4B-PH-SM4-TB | Connector Header Surface Mount 4 position 0.079" (2.00mm) |  | JST Sales America Inc. | JST
CONN21 | B4B-PH-SM4-TB(LF)(SN) | Pufferfish:B4B-PH-SM4-TB(LF)(SN) | Pufferfish:JST_B4B-PH-SM4-TB | Connector Header Surface Mount 4 position 0.079" (2.00mm) |  | JST Sales America Inc. | JST
CONN22 | B4B-PH-SM4-TB(LF)(SN) | Pufferfish:B4B-PH-SM4-TB(LF)(SN) | Pufferfish:JST_B4B-PH-SM4-TB | Connector Header Surface Mount 4 position 0.079" (2.00mm) |  | JST Sales America Inc. | JST
CONN23 | 5103308-3 | Pufferfish:5103308-3 | Pufferfish:SHDR16W66P254_2X8 | Headers & Wire Housings 16P 2 ROW HEADER LP |  |  | http://componentsearchengine.com/Datasheets/1/5103308-3.pdf
CONN24 | 5103308-3 | Pufferfish:5103308-3 | Pufferfish:SHDR16W66P254_2X8 | Headers & Wire Housings 16P 2 ROW HEADER LP |  |  | http://componentsearchengine.com/Datasheets/1/5103308-3.pdf
D1 | LED_SMD_0805 | Pufferfish:LED_SMD_0805 | Pufferfish:LED_SMD_0805 | Light emitting diode, filled shape, SMT, SMD |  |  | ~
D2 | LED_SMD_0805 | Pufferfish:LED_SMD_0805 | Pufferfish:LED_SMD_0805 | Light emitting diode, filled shape, SMT, SMD |  |  | ~
D3 | LED_SMD_0805 | Pufferfish:LED_SMD_0805 | Pufferfish:LED_SMD_0805 | Light emitting diode, filled shape, SMT, SMD |  |  | ~
DRIVE1 | TPL7407LADR | Pufferfish:TPL7407LADR | Pufferfish:SOIC127P600X175-16N | Gate Drivers 30-V, 7-Channel NMOS Array Low-Side Driver 16-SOIC -40 to 125 |  |  | http://www.ti.com/lit/gpn/tpl7407la
DRIVE2 | TPL7407LADR | Pufferfish:TPL7407LADR | Pufferfish:SOIC127P600X175-16N | Gate Drivers 30-V, 7-Channel NMOS Array Low-Side Driver 16-SOIC -40 to 125 |  |  | http://www.ti.com/lit/gpn/tpl7407la
DRIVE3 | TMC2209-SilentStepStick | Pufferfish:TMC2209-SilentStepStick | Pufferfish:MODULE_TMC2209_SilentStepStick | Stepper motor controller & driver |  | Trinamic Motion Control | https://www.trinamic.com/fileadmin/assets/Products/Eval_Documents/TMC2209_SilentStepStick_Rev1.10.pdf
DRIVE4 | TMC2209-SilentStepStick | Pufferfish:TMC2209-SilentStepStick | Pufferfish:MODULE_TMC2209_SilentStepStick | Stepper motor controller & driver |  | Trinamic Motion Control | https://www.trinamic.com/fileadmin/assets/Products/Eval_Documents/TMC2209_SilentStepStick_Rev1.10.pdf
DRIVE5 | TMC2209-SilentStepStick | Pufferfish:TMC2209-SilentStepStick | Pufferfish:MODULE_TMC2209_SilentStepStick | Stepper motor controller & driver |  | Trinamic Motion Control | https://www.trinamic.com/fileadmin/assets/Products/Eval_Documents/TMC2209_SilentStepStick_Rev1.10.pdf
DRIVE6 | TMC2209-SilentStepStick | Pufferfish:TMC2209-SilentStepStick | Pufferfish:MODULE_TMC2209_SilentStepStick | Stepper motor controller & driver |  | Trinamic Motion Control | https://www.trinamic.com/fileadmin/assets/Products/Eval_Documents/TMC2209_SilentStepStick_Rev1.10.pdf
H1 | STANDOFF_ELECTRICAL | Pufferfish:STANDOFF_ELECTRICAL | Pufferfish:STANDOFF-ELECTRICAL-NOTHERMALS
H2 | STANDOFF_ELECTRICAL | Pufferfish:STANDOFF_ELECTRICAL | Pufferfish:STANDOFF-ELECTRICAL-NOTHERMALS
H3 | STANDOFF_ELECTRICAL | Pufferfish:STANDOFF_ELECTRICAL | Pufferfish:STANDOFF-ELECTRICAL-NOTHERMALS
H4 | STANDOFF_ELECTRICAL | Pufferfish:STANDOFF_ELECTRICAL | Pufferfish:STANDOFF-ELECTRICAL-NOTHERMALS
H5 | STANDOFF_ELECTRICAL | Pufferfish:STANDOFF_ELECTRICAL | Pufferfish:STANDOFF-ELECTRICAL-NOTHERMALS
H6 | STANDOFF_ELECTRICAL | Pufferfish:STANDOFF_ELECTRICAL | Pufferfish:STANDOFF-ELECTRICAL-NOTHERMALS
IC1 | TCA9548APWR | Pufferfish:TCA9548APWR | Pufferfish:SOP65P640X120-24N | TEXAS INSTRUMENTS - TCA9548APWR - I2C SWITCH W/ RESET, 8-CH, TSSOP-24 |  |  | http://www.ti.com/lit/ds/symlink/tca9548a.pdf
IC2 | TCA9548APWR | Pufferfish:TCA9548APWR | Pufferfish:SOP65P640X120-24N | TEXAS INSTRUMENTS - TCA9548APWR - I2C SWITCH W/ RESET, 8-CH, TSSOP-24 |  |  | http://www.ti.com/lit/ds/symlink/tca9548a.pdf
IC3 | LMP91000SDE | Pufferfish:LMP91000SDE | Pufferfish:SON50P400X400X80-15N | Texas Instruments,LMP91000SDE/NOPB,AFE LMP91000SDE/NOPB, Analogue Front End IC, 1-channel Serial-I2C, 14-Pin WSON |  |  | http://www.ti.com/lit/ds/symlink/lmp91000.pdf
IC4 | W25Q16JVSSIQ | Pufferfish:W25Q16JVSSIQ | Pufferfish:SOIC127P790X216-8N | NOR Flash spiFlash, 3V, 16M-bit, 4Kb Uniform Sector |  |  | https://www.winbond.com/resource-files/w25q16jv%20spi%20revd%2008122016.pdf
J1 | TERMINAL_SCREW_4_2.54mm | Pufferfish:TERMINAL_SCREW_4_2.54mm | Pufferfish:TERMINAL_PIN_4_2.54mm | Screw terminal, connector, 4x1 pin, 2.54mm
J2 | TERMINAL_SCREW_4_2.54mm | Pufferfish:TERMINAL_SCREW_4_2.54mm | Pufferfish:TERMINAL_PIN_4_2.54mm | Screw terminal, connector, 4x1 pin, 2.54mm
J3 | TERMINAL_SCREW_8_2.54mm | Pufferfish:TERMINAL_SCREW_8_2.54mm | Pufferfish:TERMINAL_PIN_8_2.54mm | Screw terminal, connector, 8x1 pin, 2.54mm
J4 | TERMINAL_SCREW_4_2.54mm | Pufferfish:TERMINAL_SCREW_4_2.54mm | Pufferfish:TERMINAL_PIN_4_2.54mm | Screw terminal, connector, 4x1 pin, 2.54mm
L1 | LOGO_PUFFERFISH | Pufferfish:LOGO_PUFFERFISH | Pufferfish:LOGO_PUFFERFISH
MOD1 | NUCLEO-F429ZI | Pufferfish:NUCLEO-F429ZI | Pufferfish:MODULE_NUCLEO-F429ZI | STM32 Nucleo-144 development board with STM32F429ZIT6 MCU, supports Arduino, ST Zio and Morpho |  | STMicroelectronics | https://www.st.com/en/evaluation-tools/nucleo-h743zi.html
PRESS1 | ABPMAND001PG2A3 | Pufferfish:ABPMAND001PG2A3 | Pufferfish:ABPMANN030PG2A3 | ABPMAND001PG2A3, Differential Pressure Sensor 1psi 6-Pin SMT |  |  | https://www.mouser.com/datasheet/2/187/honeywell-sensing-pressure-board-mount-abp-series--1846114.pdf |  |  |  | 0-1psi
PRESS2 | ABPMAND001PG2A3 | Pufferfish:ABPMAND001PG2A3 | Pufferfish:ABPMANN030PG2A3 | ABPMAND001PG2A3, Differential Pressure Sensor 1psi 6-Pin SMT |  |  | https://www.mouser.com/datasheet/2/187/honeywell-sensing-pressure-board-mount-abp-series--1846114.pdf |  |  |  | 0-1psi
PRESS3 | ABPMAND001PG2A3 | Pufferfish:ABPMAND001PG2A3 | Pufferfish:ABPMANN030PG2A3 | ABPMAND001PG2A3, Differential Pressure Sensor 1psi 6-Pin SMT |  |  | https://www.mouser.com/datasheet/2/187/honeywell-sensing-pressure-board-mount-abp-series--1846114.pdf |  |  |  | 0-1psi
PRESS4 | HSCMRRN100MDSA3 | Pufferfish:HSCMRRN100MDSA3 | Pufferfish:PRESSURE_HSC_SOIC-8 | Board Mount Pressure Sensors SMT, Dual Rad Barbed Differential, 3.3V |  | Honeywell | https://www.mouser.com/datasheet/2/187/honeywell-sensing-trustability-hsc-series-high-acc-708740.pdf |  |  |  | ±100mbar
PRESS5 | HSCMRRN100MDSA3 | Pufferfish:HSCMRRN100MDSA3 | Pufferfish:PRESSURE_HSC_SOIC-8 | Board Mount Pressure Sensors SMT, Dual Rad Barbed Differential, 3.3V |  | Honeywell | https://www.mouser.com/datasheet/2/187/honeywell-sensing-trustability-hsc-series-high-acc-708740.pdf |  |  |  | ±100mbar
PRESS6 | HSCMRRN100MDSA3 | Pufferfish:HSCMRRN100MDSA3 | Pufferfish:PRESSURE_HSC_SOIC-8 | Board Mount Pressure Sensors SMT, Dual Rad Barbed Differential, 3.3V |  | Honeywell | https://www.mouser.com/datasheet/2/187/honeywell-sensing-trustability-hsc-series-high-acc-708740.pdf |  |  |  | ±100mbar
PRESS7 | ABPMANN030PG2A3 | Pufferfish:ABPMANN030PG2A3 | Pufferfish:ABPMANN030PG2A3 | ABPMANN030PG2A3, Differential Pressure Sensor 30psi 6-Pin SMT |  |  | https://www.mouser.com/datasheet/2/187/honeywell-sensing-pressure-board-mount-abp-series--1846114.pdf |  |  |  | 0-30psi
PRESS8 | ABPMANN030PG2A3 | Pufferfish:ABPMANN030PG2A3 | Pufferfish:ABPMANN030PG2A3 | ABPMANN030PG2A3, Differential Pressure Sensor 30psi 6-Pin SMT |  |  | https://www.mouser.com/datasheet/2/187/honeywell-sensing-pressure-board-mount-abp-series--1846114.pdf |  |  |  | 0-30psi
PRESS9 | ABPMAND001PG2A3 | Pufferfish:ABPMAND001PG2A3 | Pufferfish:ABPMANN030PG2A3 | ABPMAND001PG2A3, Differential Pressure Sensor 1psi 6-Pin SMT |  |  | https://www.mouser.com/datasheet/2/187/honeywell-sensing-pressure-board-mount-abp-series--1846114.pdf |  |  |  | 0-1psi
PRESS10 | HSCMRRN060PDSA3 | Pufferfish:HSCMRRN060PDSA3 | Pufferfish:PRESSURE_HSC_SOIC-8 | Board Mount Pressure Sensors SMT, Dual Rad Barbed Differential, 3.3V Board Mount Pressure Sensors SMT, Dual Rad Barbed Differential, 3.3V |  | Honeywell | https://www.mouser.com/datasheet/2/187/honeywell-sensing-trustability-hsc-series-high-acc-708740.pdf |  |  |  | ±60psi
PRESS11 | HSCMRRN060PDSA3 | Pufferfish:HSCMRRN060PDSA3 | Pufferfish:PRESSURE_HSC_SOIC-8 | Board Mount Pressure Sensors SMT, Dual Rad Barbed Differential, 3.3V Board Mount Pressure Sensors SMT, Dual Rad Barbed Differential, 3.3V |  | Honeywell | https://www.mouser.com/datasheet/2/187/honeywell-sensing-trustability-hsc-series-high-acc-708740.pdf |  |  |  | ±60psi
PRESS12 | HSCMRRN060PDSA3 | Pufferfish:HSCMRRN060PDSA3 | Pufferfish:PRESSURE_HSC_SOIC-8 | Board Mount Pressure Sensors SMT, Dual Rad Barbed Differential, 3.3V Board Mount Pressure Sensors SMT, Dual Rad Barbed Differential, 3.3V |  | Honeywell | https://www.mouser.com/datasheet/2/187/honeywell-sensing-trustability-hsc-series-high-acc-708740.pdf |  |  |  | ±60psi
PRESS13 | SDP810-125PA | Pufferfish:SDP810-125PA | Pufferfish:PRESSURE_SDP81x | Sensirion SDP810-125PA, Differential Pressure Sensor +125Pa 4-Pin |  | Sensirion | https://www.mouser.com/datasheet/2/682/Sensirion_Differential_Pressure_Sensors_SDP8xx_Dig-1511125.pdf |  |  |  | ±125Pa
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

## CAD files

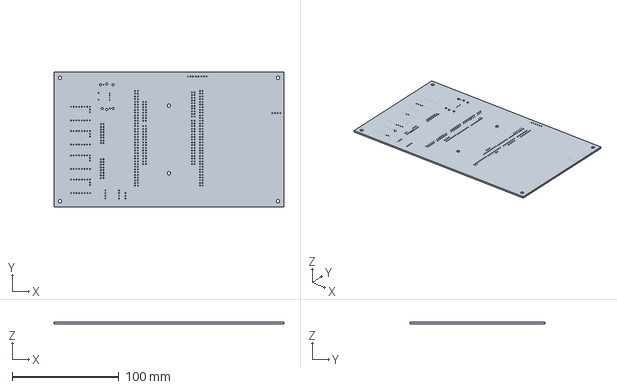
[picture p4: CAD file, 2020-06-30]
designs/Pufferfish-Controller-1/exports/Pufferfish-Controller-1.step
216.0 x 127.0 x 1.60 mm

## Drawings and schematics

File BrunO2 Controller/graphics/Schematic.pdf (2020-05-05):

# 5V GND

# 3.3V GND

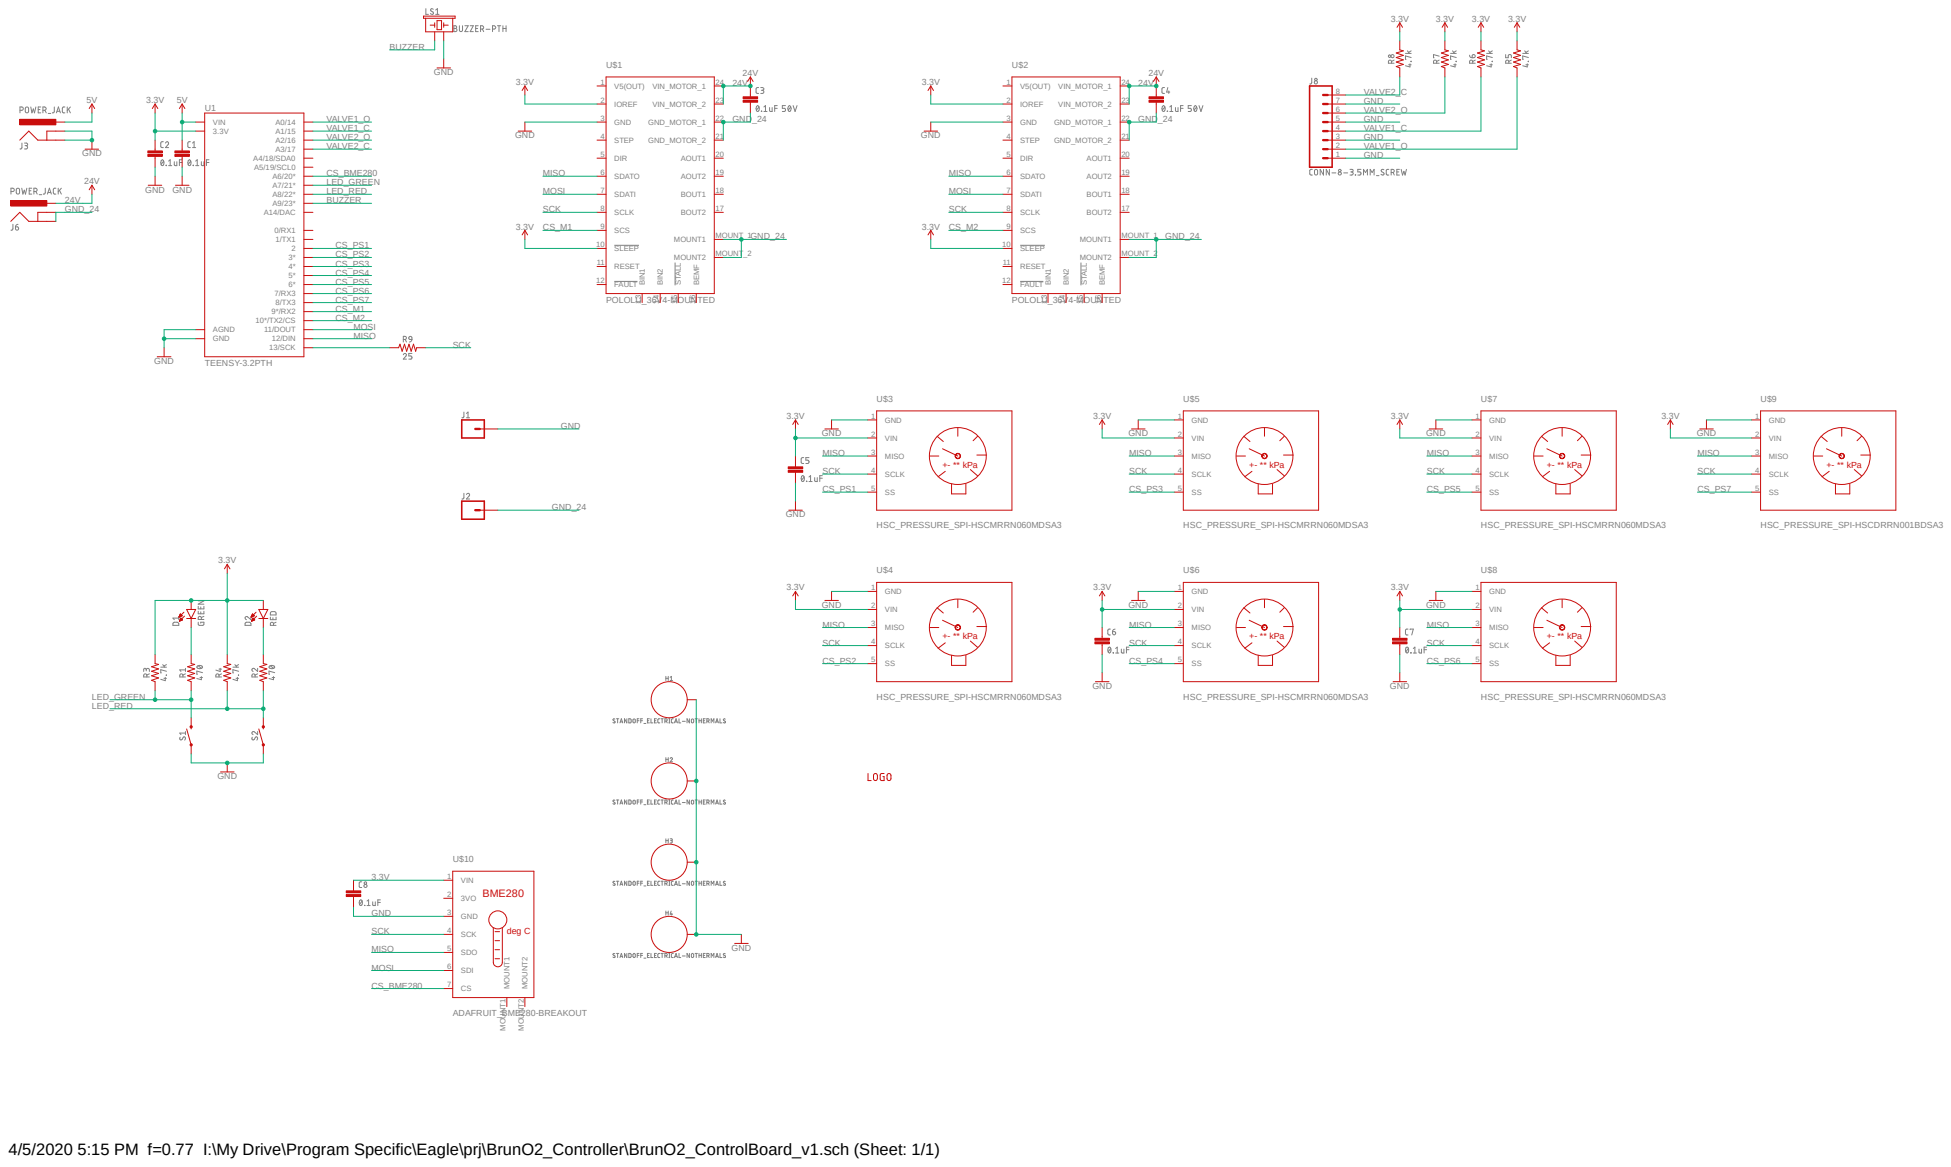
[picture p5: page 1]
TEENSY-3.2PTH; POLOLU_36V4-MOUNTED; GND; 3.3V GND; HSC_PRESSURE_SPI-HSCMRRN060MDSA3; HSC_PRESSURE_SPI-HSCDRRN001BDSA3 GND; GND GND; ADAFRUIT_BME280-BREAKOUT; 8/TX3 9*/RX2 10*/TX2/CS 11/DOUT 12/DIN 13/SCK; A0/14 A1/15 A2/16 A3/17 A4/18/SDA0 A5/19/SCL0 A6/20* A7/21* A8/22* A9/23* A14/DAC; AGND GND; VIN; IOREF 2; GND 3; SDATO 6; SDATI 7; SCLK 8; SCS 9; SLEEP 10; V5(OUT) 1; STEP 4; DIR 5; RESET 11; FAULT 12; BIN¹ 13; BIN² 14; STALL 15; BEMF 16 VIN_MOTOR_1; 24 VIN_MOTOR_2; 23 GND_MOTOR_1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

GND GND GND GND GND

4/5/2020 5:15 PM f=0.77 I:\My Drive\Program Specific\Eagle\prj\BrunO2_Controller\BrunO2_ControlBoard_v1.sch (Sheet: 1/1)

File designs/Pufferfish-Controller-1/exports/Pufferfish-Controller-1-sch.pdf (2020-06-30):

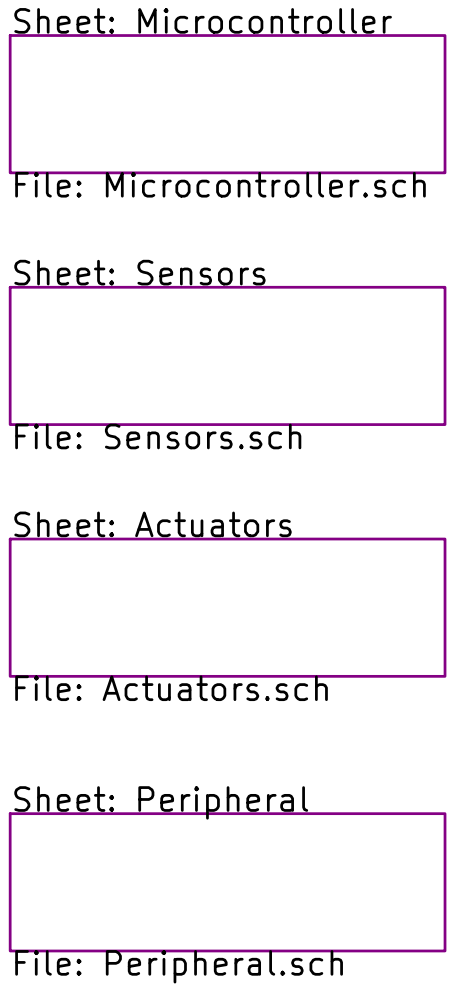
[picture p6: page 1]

Sheet: Microcontroller File: Microcontroller.sch Sheet: Sensors File: Sensors.sch Sheet: Actuators File: Actuators.sch Sheet: Peripheral

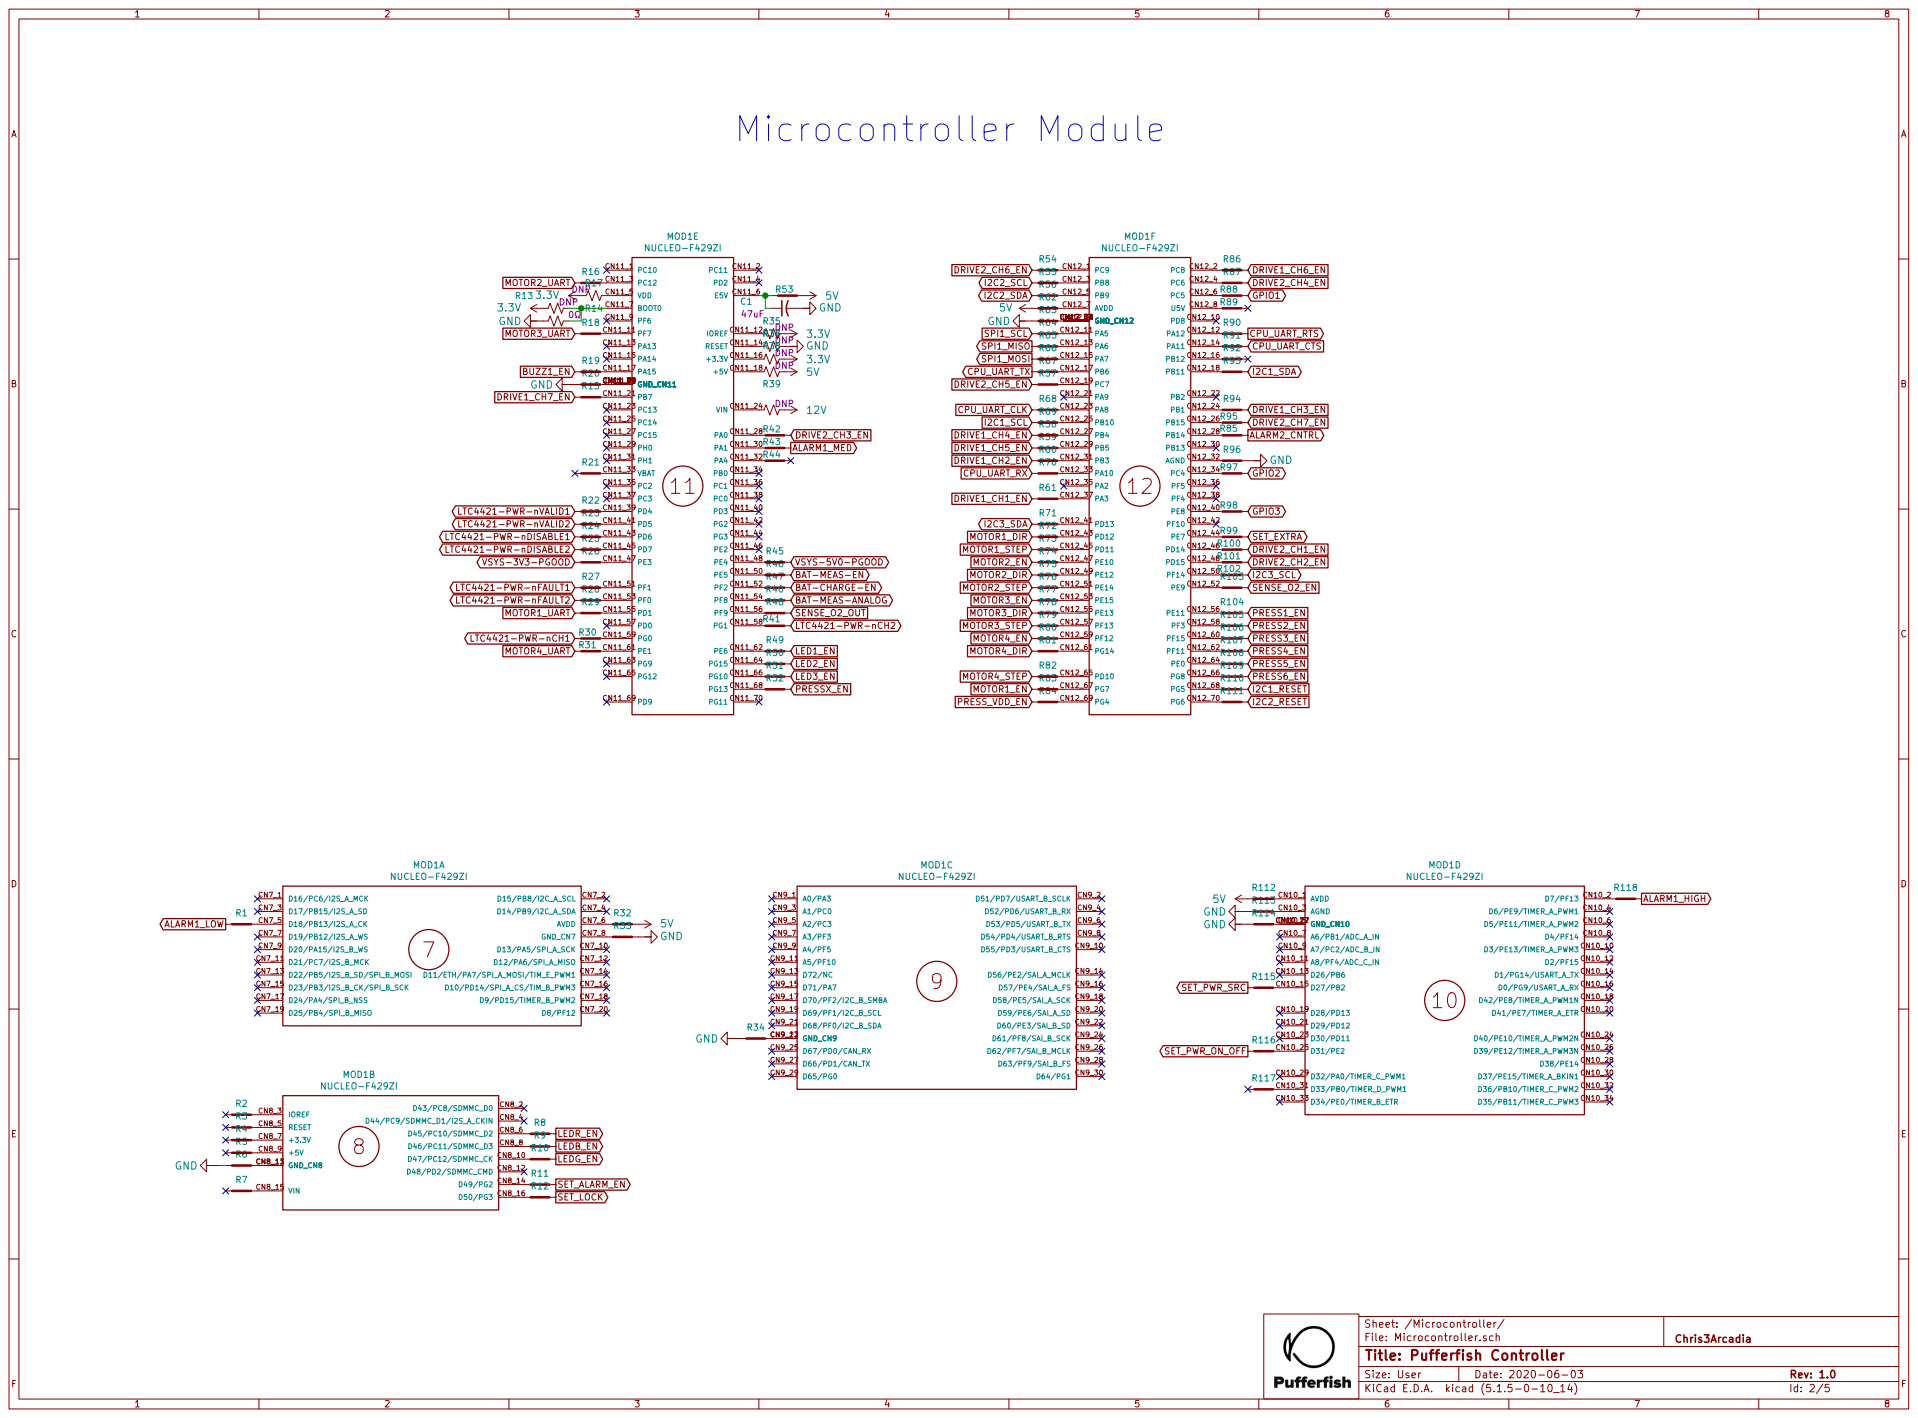
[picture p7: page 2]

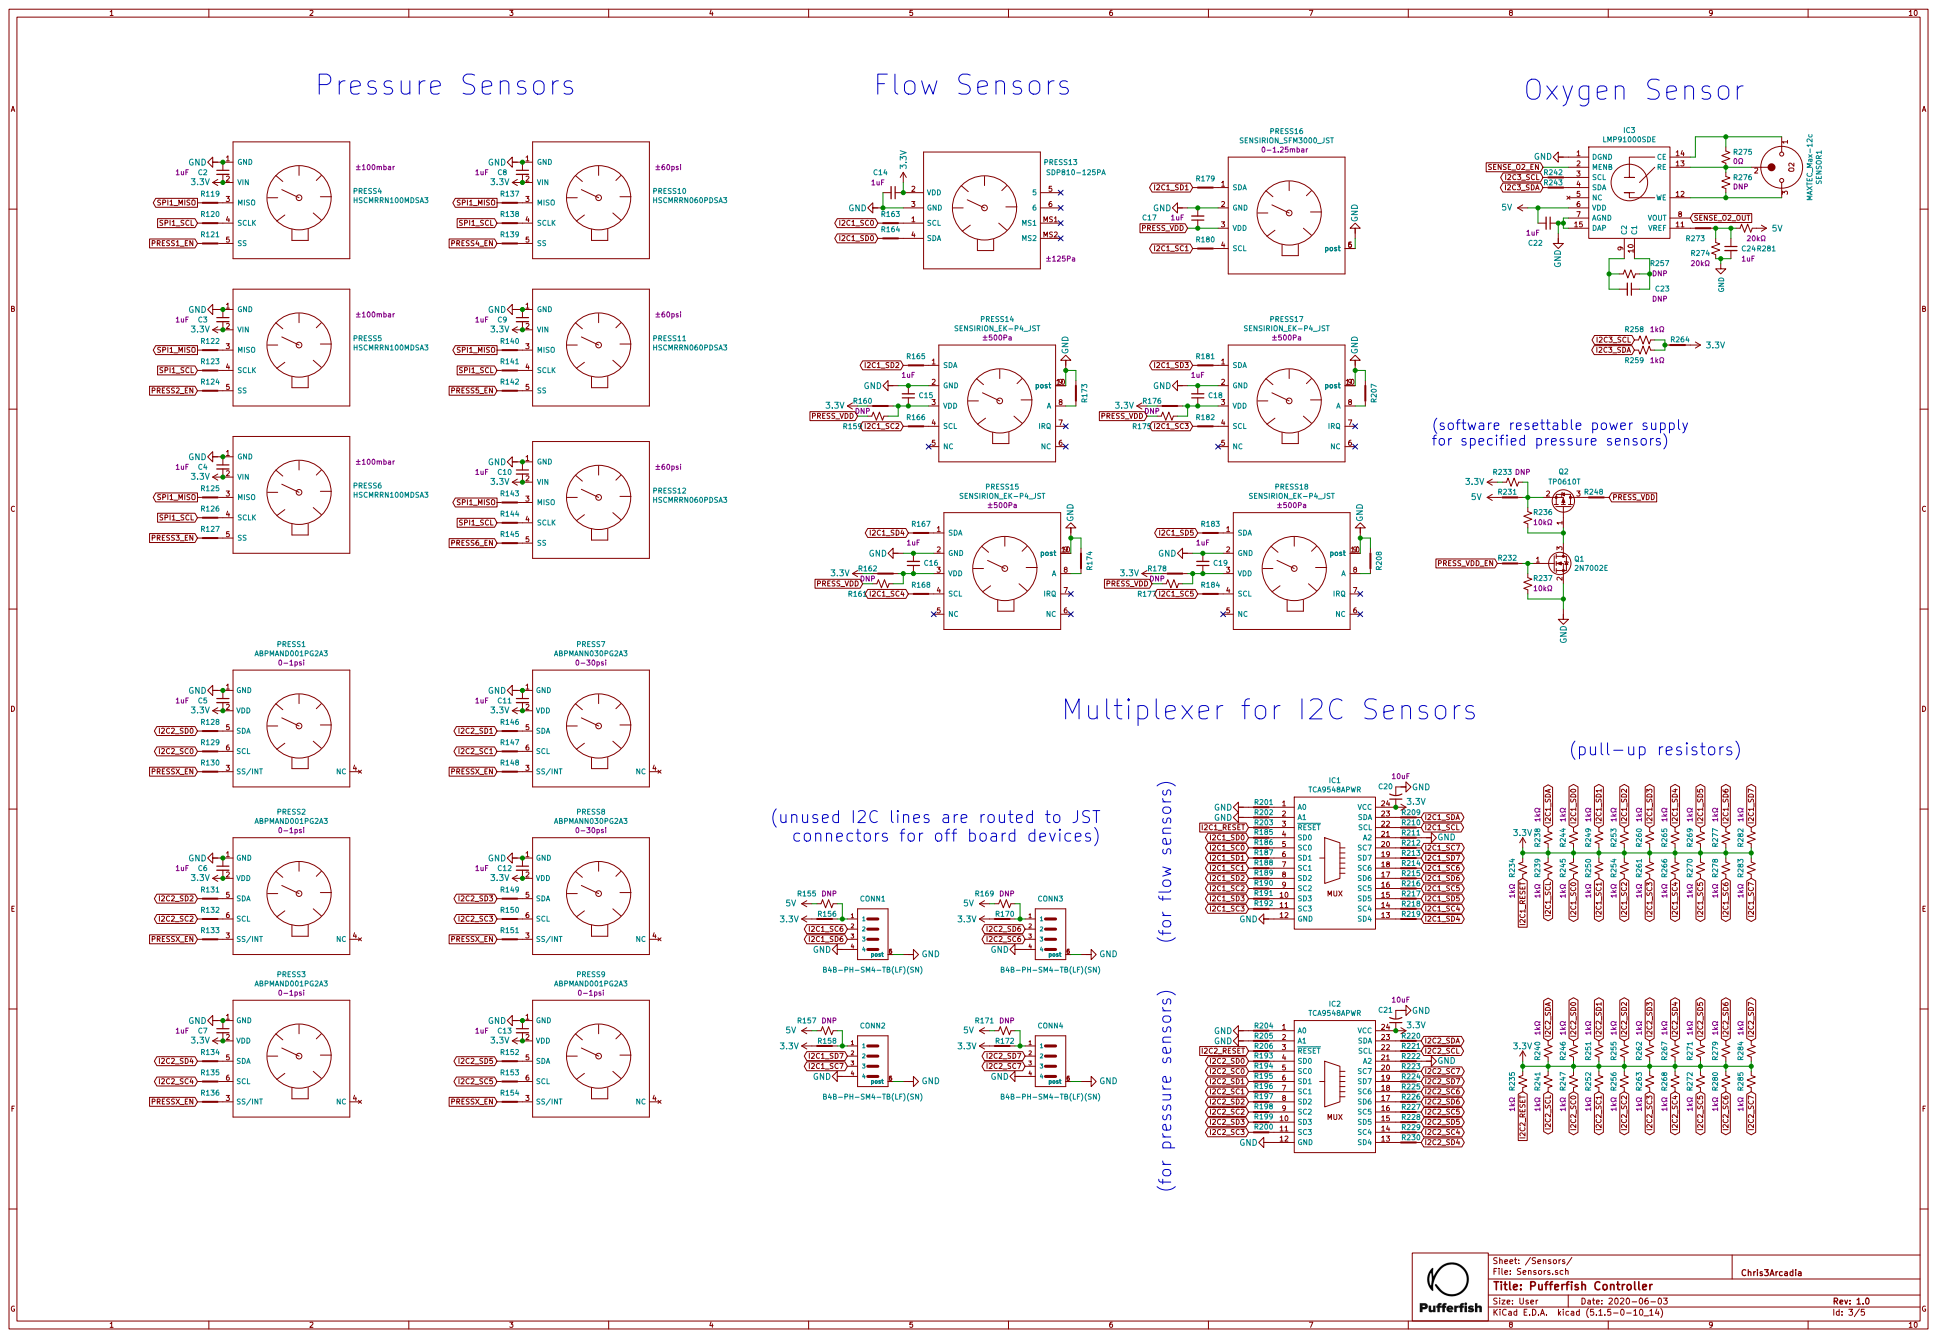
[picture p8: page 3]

for specified pressure sensors) (for pressure sensors) (for flow sensors)

(software resettable power supply

(unused I2C lines are routed to JST
connectors for off board devices)

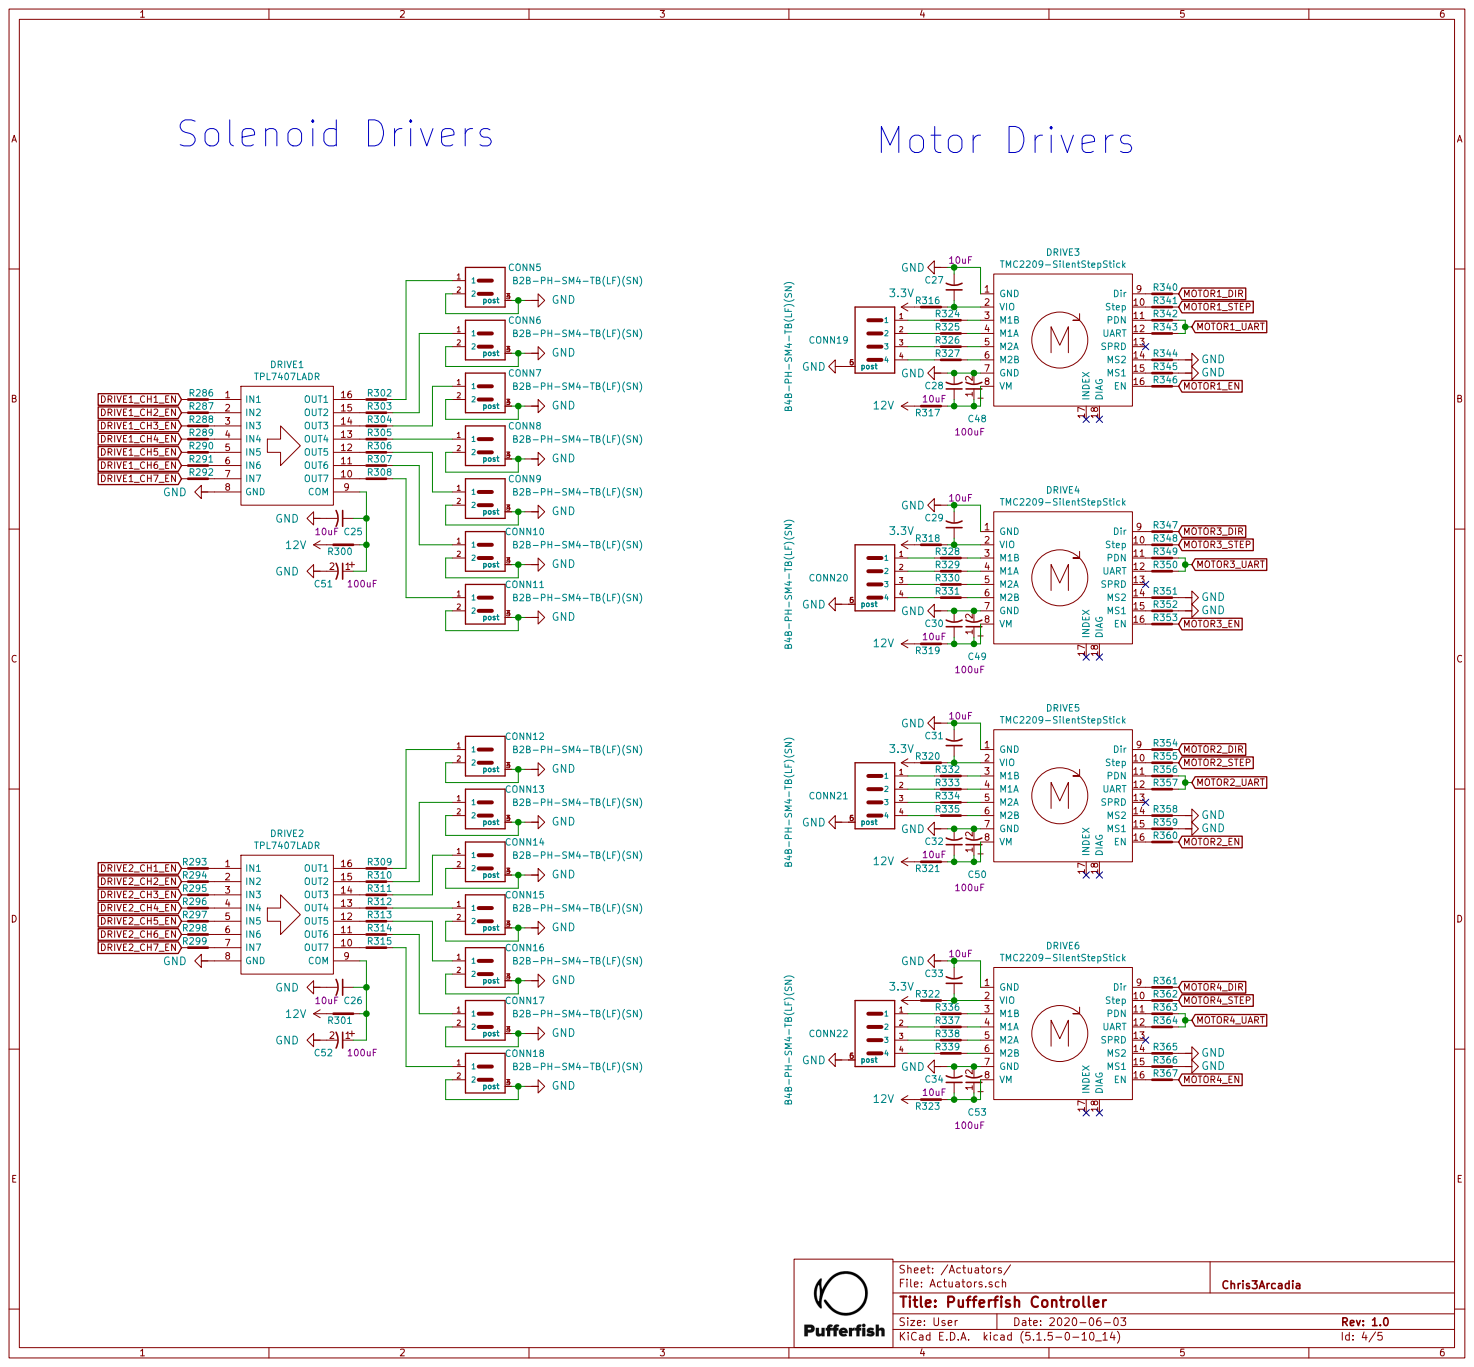
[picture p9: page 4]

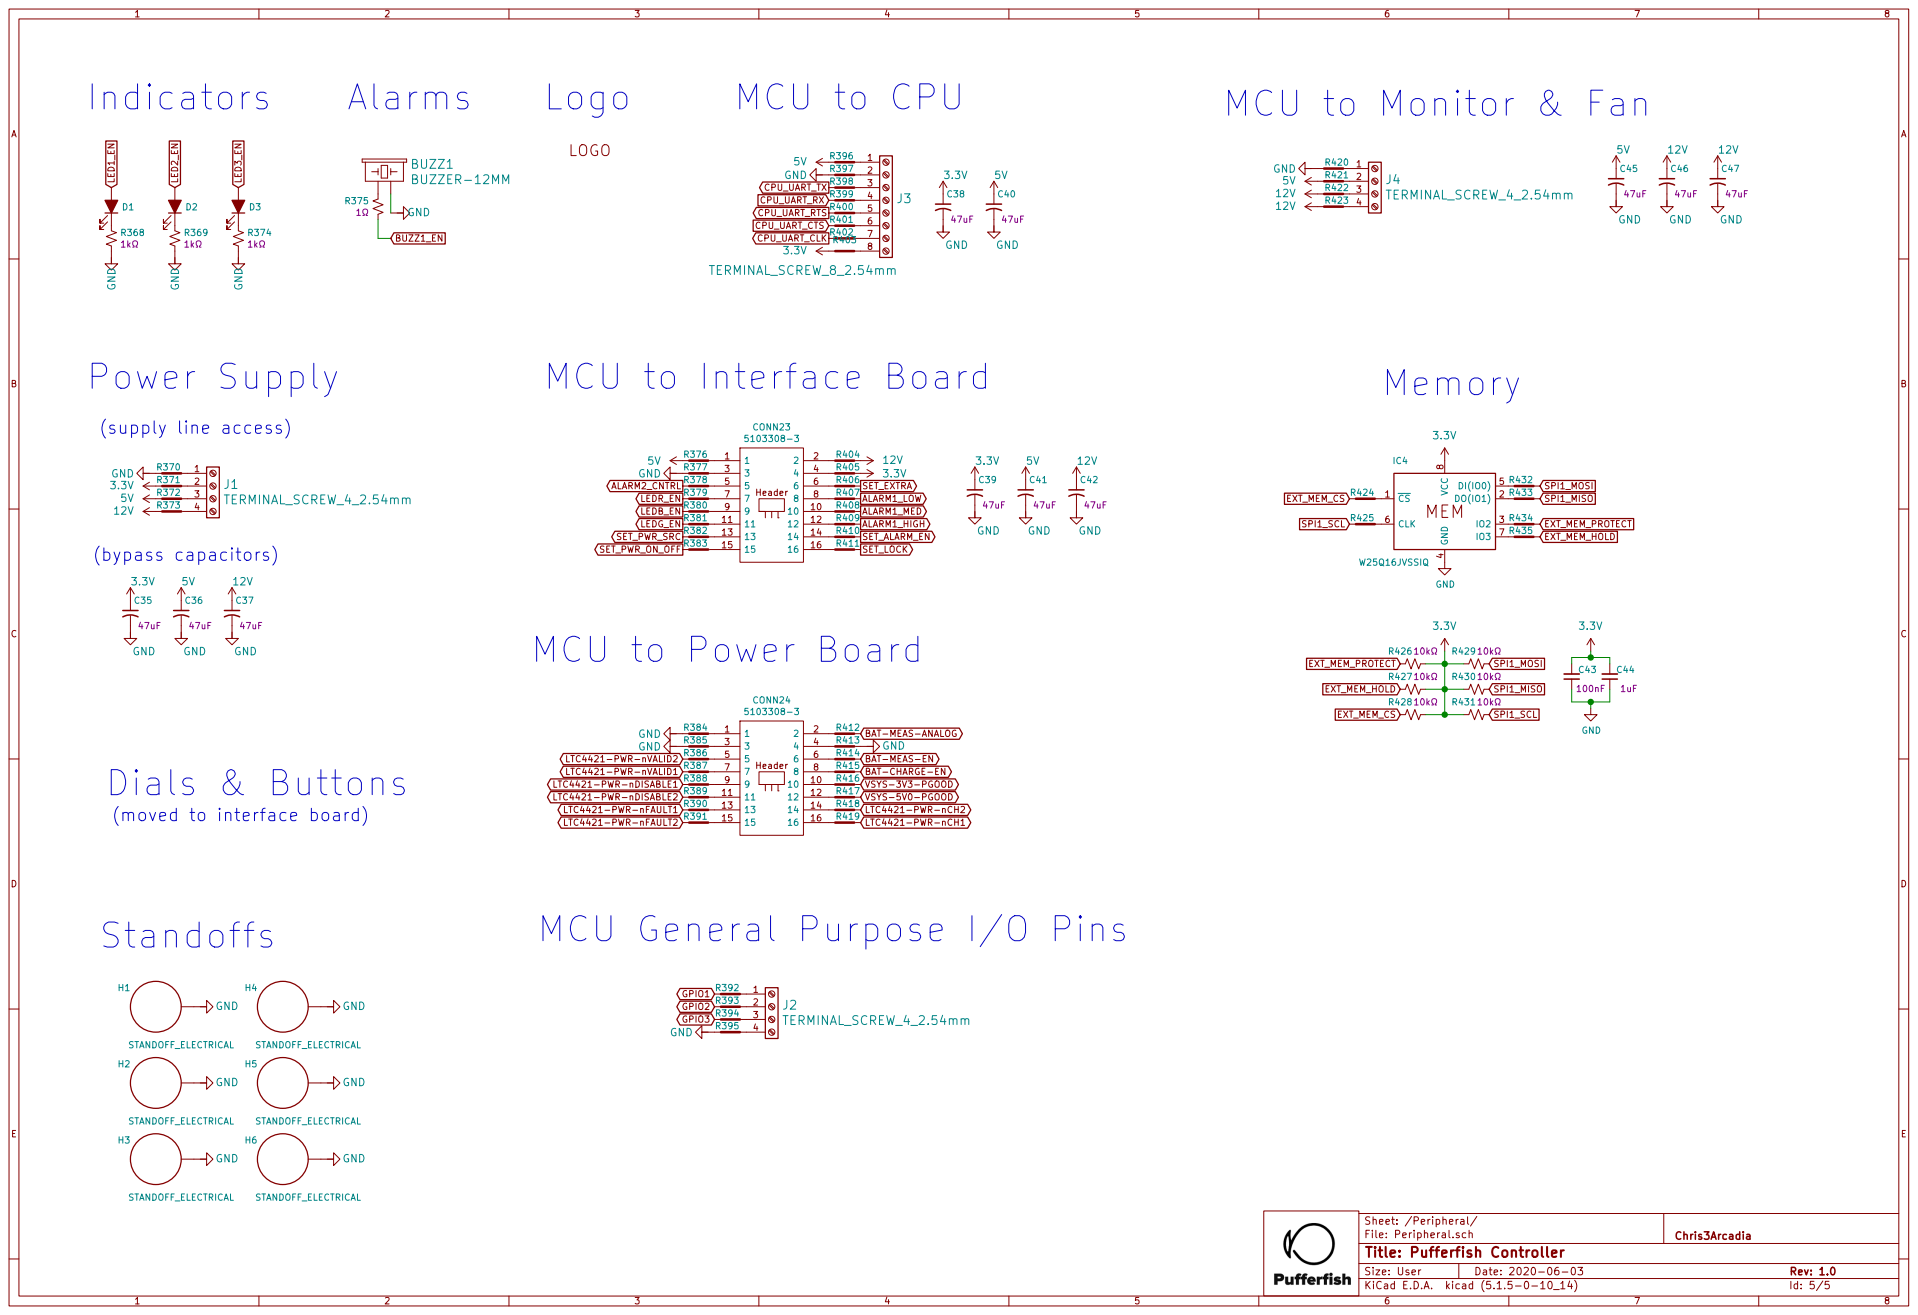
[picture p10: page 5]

ALARM2_CNTRL
LEDR_EN MCU General Purpose I/O Pins

MCU to Power Board

(moved to interface board)

File: Peripheral.sch
Id: 5/5 Title: Pufferfish Controller

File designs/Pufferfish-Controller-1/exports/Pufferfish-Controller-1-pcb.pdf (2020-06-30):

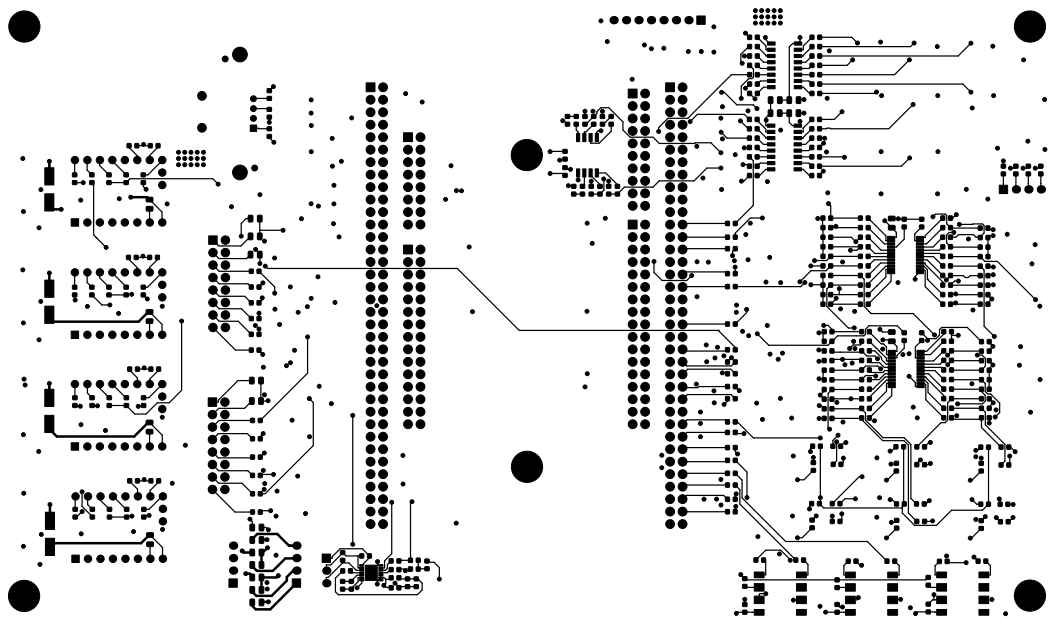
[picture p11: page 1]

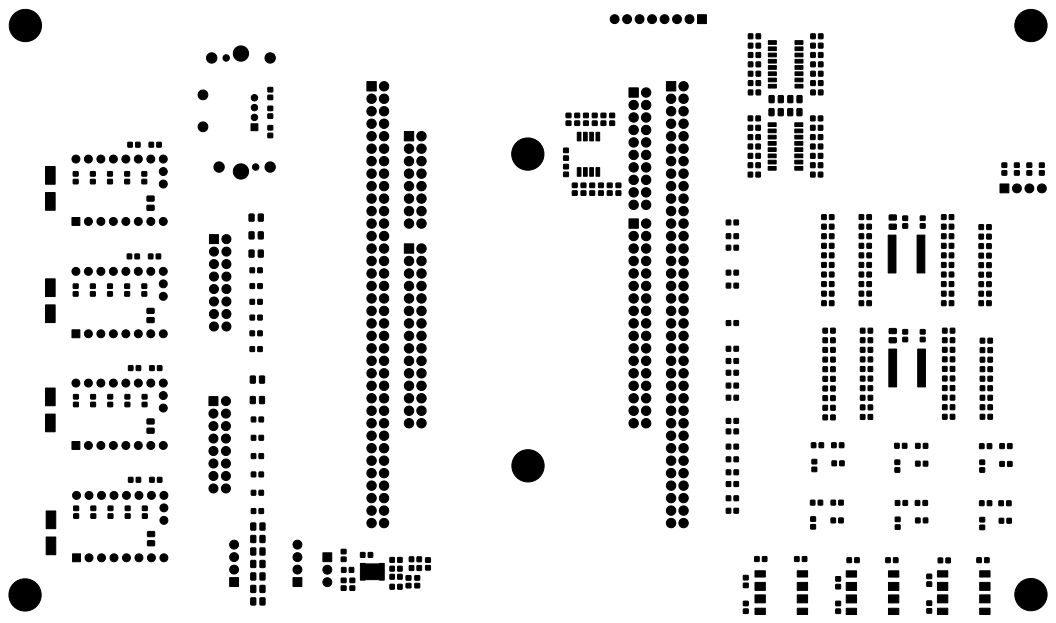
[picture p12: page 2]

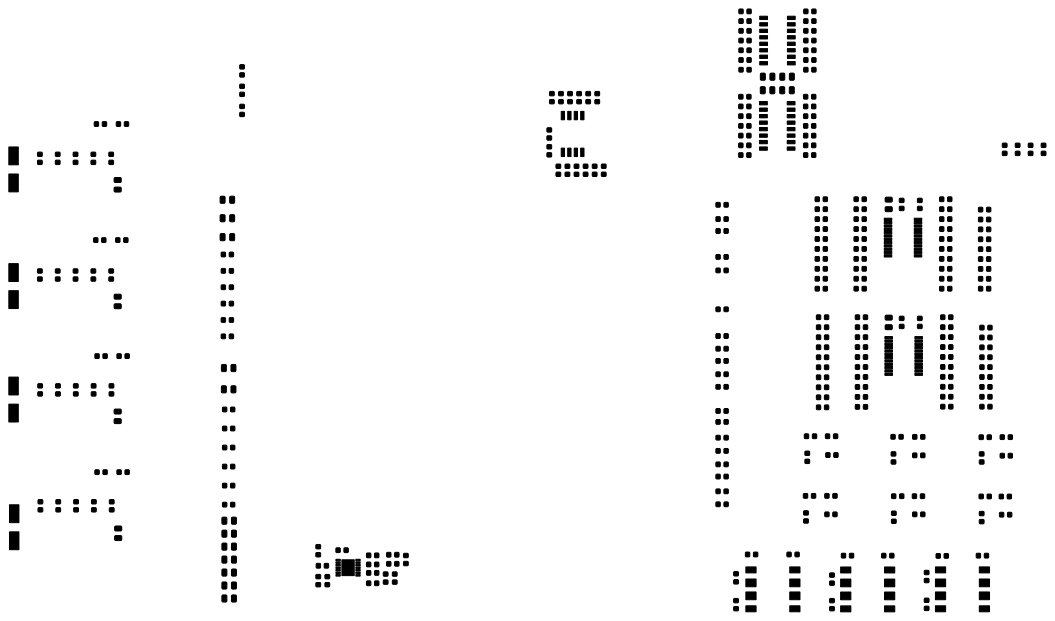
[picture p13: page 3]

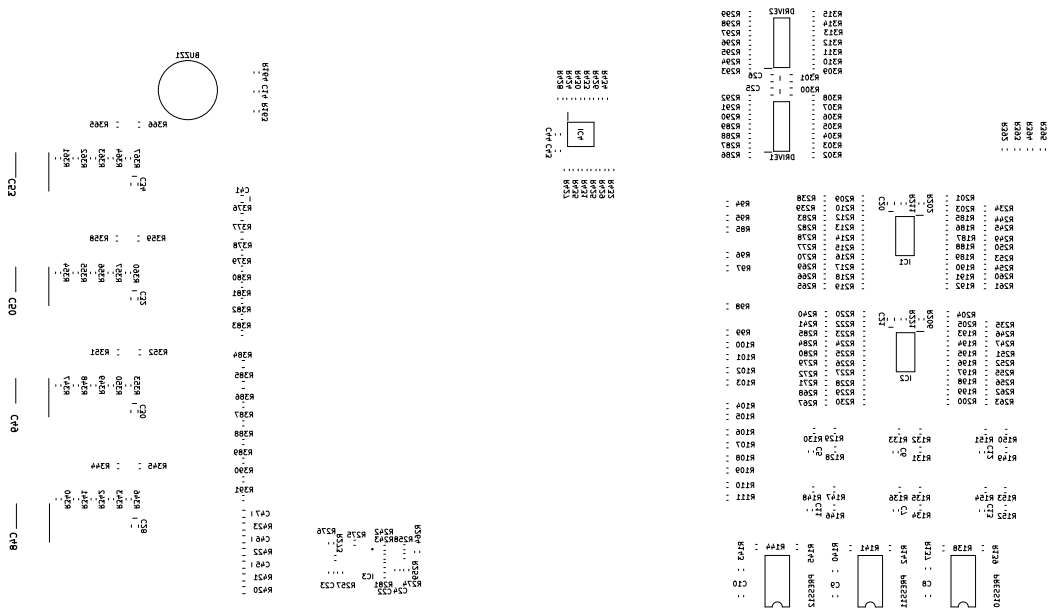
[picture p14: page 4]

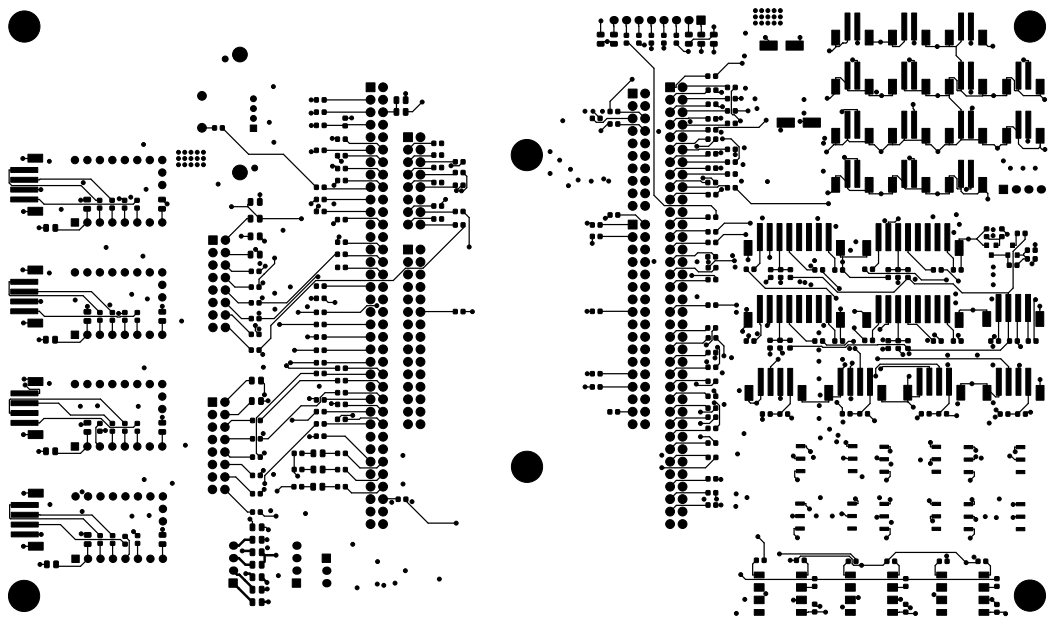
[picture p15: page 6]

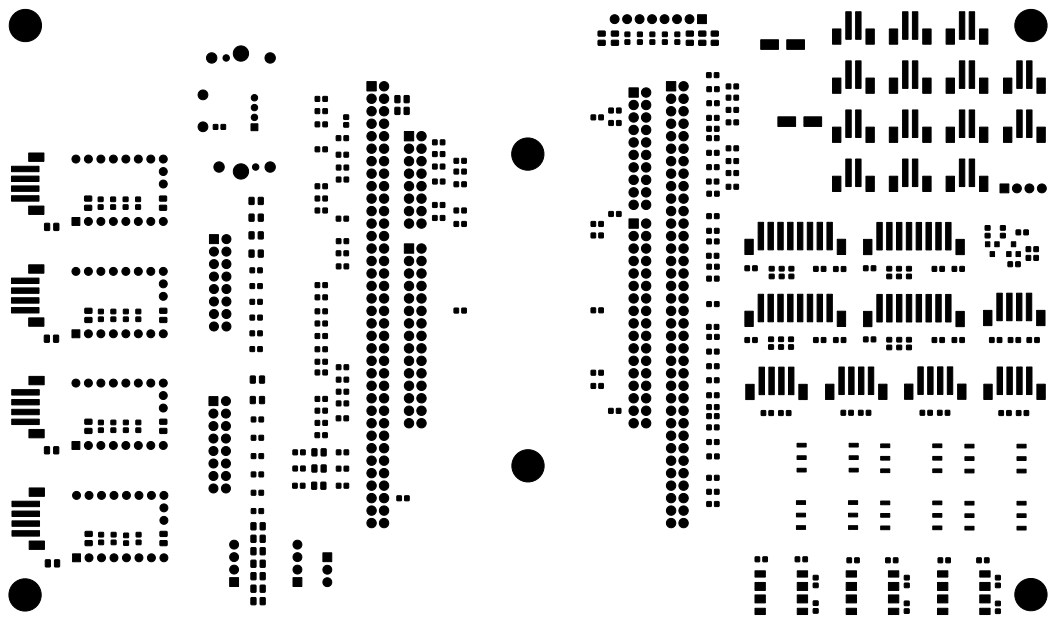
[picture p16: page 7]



Pez Globo Pufferfish Controller v1.0 Chris3Arcadia (2020/06/29)





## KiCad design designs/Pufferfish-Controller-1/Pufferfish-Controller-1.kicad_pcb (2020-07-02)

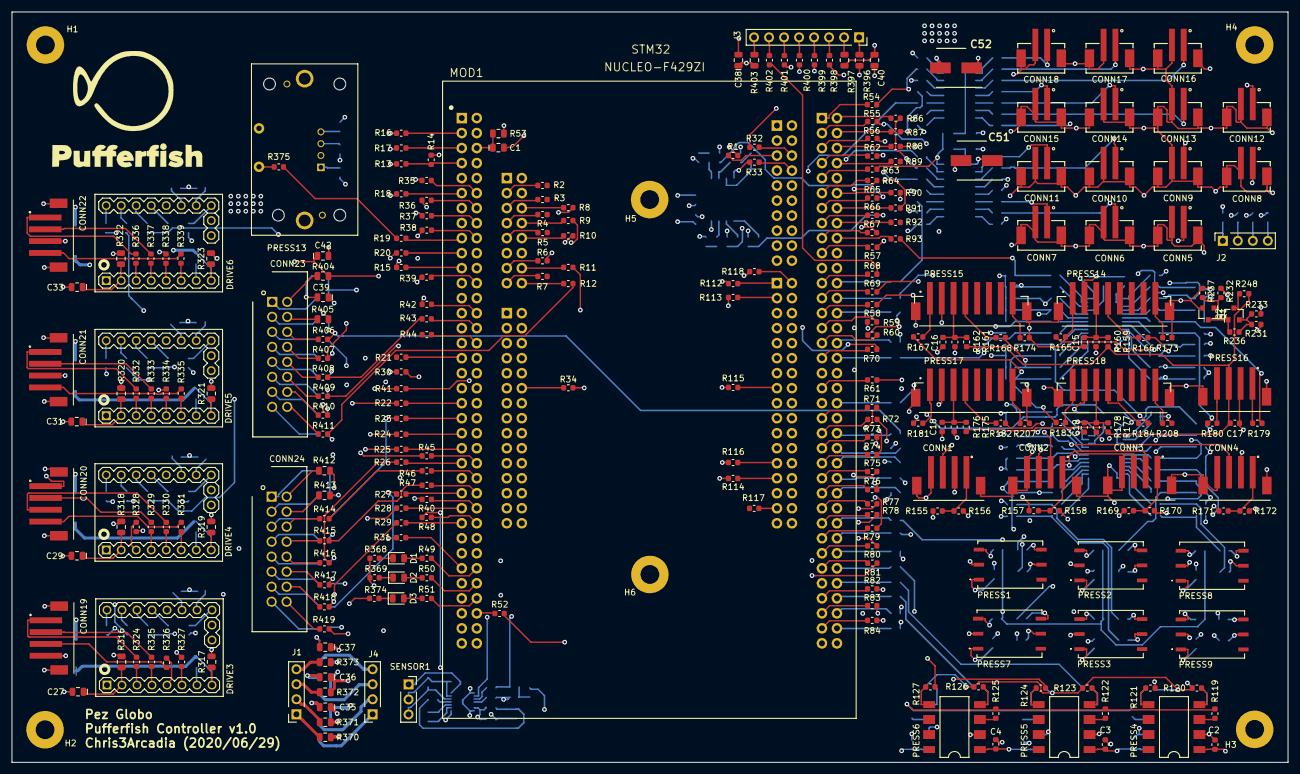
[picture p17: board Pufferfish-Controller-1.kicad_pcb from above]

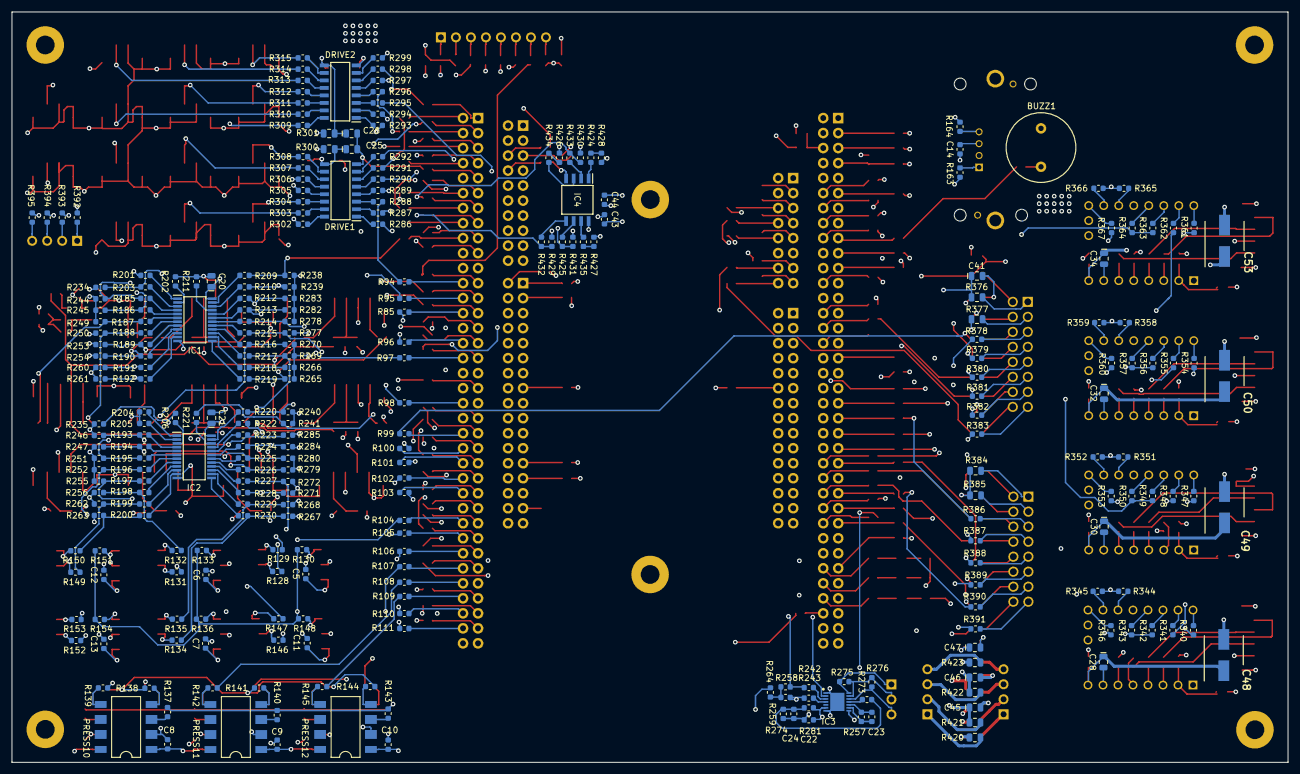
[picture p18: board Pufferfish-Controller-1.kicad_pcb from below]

Board: 6 copper layers, 216.0 x 127.0 mm, 559 parts (276 on the bottom side), 537 nets.

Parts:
BUZZ1: BUZZER-12MM
C1, C20, C21, C25, C26, C27, C28, C29, C30, C31, C32, C33, C34, C35, C36, C37, C38, C39, C40, C41, C42, C45, C46, C47: CAP_POLAR_SMD_0805
C2, C3, C4, C5, C6, C7, C8, C9, C10, C11, C12, C13, C14, C15, C16, C17, C18, C19, C22, C23, C24, C43, C44: CAP_SMD_0603
C48, C49, C50, C51, C52, C53: UCQ1E101MCL1GS; CAPAE660X820N
CONN1, CONN2, CONN3, CONN4, CONN19, CONN20, CONN21, CONN22: B4B-PH-SM4-TB(LF)(SN); JST_B4B-PH-SM4-TB
CONN5, CONN6, CONN7, CONN8, CONN9, CONN10, CONN11, CONN12, CONN13, CONN14, CONN15, CONN16, CONN17, CONN18: B2B-PH-SM4-TB(LF)(SN); JST_B2B-PH-SM4-TB
CONN23, CONN24: 5103308-3; SHDR16W66P254_2X8
D1, D2, D3: LED_SMD_0805
DRIVE1, DRIVE2: TPL7407LADR; SOIC127P600X175-16N
DRIVE3, DRIVE4, DRIVE5, DRIVE6: TMC2209-SilentStepStick; MODULE_TMC2209_SilentStepStick
H1, H2, H3, H4, H5, H6: STANDOFF_ELECTRICAL; STANDOFF-ELECTRICAL-NOTHERMALS
IC1, IC2: TCA9548APWR; SOP65P640X120-24N
IC3: LMP91000SDE; SON50P400X400X80-15N
IC4: W25Q16JVSSIQ; SOIC127P790X216-8N
J1, J2, J4: TERMINAL_SCREW_4_2.54mm; TERMINAL_PIN_4_2.54mm
J3: TERMINAL_SCREW_8_2.54mm; TERMINAL_PIN_8_2.54mm
L1: LOGO_PUFFERFISH
MOD1: NUCLEO-F429ZI; MODULE_NUCLEO-F429ZI
PRESS1, PRESS2, PRESS3, PRESS9: ABPMAND001PG2A3; ABPMANN030PG2A3
PRESS4, PRESS5, PRESS6: HSCMRRN100MDSA3; PRESSURE_HSC_SOIC-8
PRESS7, PRESS8: ABPMANN030PG2A3
PRESS10, PRESS11, PRESS12: HSCMRRN060PDSA3; PRESSURE_HSC_SOIC-8
PRESS13: SDP810-125PA; PRESSURE_SDP81x
PRESS14, PRESS15, PRESS17, PRESS18: SENSIRION_EK-P4_JST; SENSIRION_EK-P_JST
PRESS16: SENSIRION_SFM3000_JST
Q1: 2N7002E; SOT-23
Q2: TP0610T; SOT-23
R1, R2, R3, R4, R5, R6, R7, R8, R9, R10, R11, R12, R15, R16, R18, R19, R20, R21, R22, R23, R24, R25, R26, R27, R28, R29, R30, R31, R32, R33, R34, R40, R41, R42, R43, R44, R45, R46, R47, R48, R49, R50, R51, R52, R54, R55, R56, R57, R58, R59, R60, R61, R62, R63, R64, R65, R66, R67, R68, R69, R70, R71, R72, R73, R74, R75, R76, R77, R78, R79, R80, R81, R82, R83, R84, R85, R86, R87, R88, R89, R90, R91, R92, R93, R94, R95, R96, R97, R98, R99, R100, R101, R102, R103, R104, R105, R106, R107, R108, R109, R110, R111, R112, R113, R114, R115, R116, R117, R118, R119, R120, R121, R122, R123, R124, R125, R126, R127, R128, R129, R130, R131, R132, R133, R134, R135, R136, R137, R138, R139, R140, R141, R142, R143, R144, R145, R146, R147, R148, R149, R150, R151, R152, R153, R154, R156, R158, R160, R162, R163, R164, R165, R166, R167, R168, R170, R172, R173, R174, R176, R178, R179, R180, R181, R182, R183, R184, R185, R186, R187, R188, R189, R190, R191, R192, R193, R194, R195, R196, R197, R198, R199, R200, R201, R202, R203, R204, R205, R206, R207, R208, R209, R210, R211, R212, R213, R214, R215, R216, R217, R218, R219, R220, R221, R222, R223, R224, R225, R226, R227, R228, R229, R230, R231, R232, R242, R243, R248, R264, R273, R286, R287, R288, R289, R290, R291, R292, R293, R294, R295, R296, R297, R298, R299, R302, R303, R304, R305, R306, R307, R308, R309, R310, R311, R312, R313, R314, R315, R324, R325, R326, R327, R328, R329, R330, R331, R332, R333, R334, R335, R336, R337, R338, R339, R340, R341, R342, R343, R344, R345, R346, R347, R348, R349, R350, R351, R352, R353, R354, R355, R356, R357, R358, R359, R360, R361, R362, R363, R364, R365, R366, R367, R378, R379, R380, R381, R382, R383, R386, R387, R388, R389, R390, R391, R392, R393, R394, R395, R398, R399, R400, R401, R402, R406, R407, R408, R409, R410, R411, R414, R415, R416, R417, R418, R419, R424, R425, R432, R433, R434, R435: SHORT_SMD_0603
R13, R14, R17, R35, R36, R37, R38, R39, R155, R157, R159, R161, R169, R171, R175, R177, R233, R234, R235, R236, R237, R238, R239, R240, R241, R244, R245, R246, R247, R249, R250, R251, R252, R253, R254, R255, R256, R257, R258, R259, R260, R261, R262, R263, R265, R266, R267, R268, R269, R270, R271, R272, R274, R275, R276, R277, R278, R279, R280, R281, R282, R283, R284, R285, R368, R369, R374, R375, R426, R427, R428, R429, R430, R431: RES_SMD_0603
R53, R300, R301, R316, R317, R318, R319, R320, R321, R322, R323, R370, R371, R372, R373, R376, R377, R384, R385, R396, R397, R403, R404, R405, R412, R413, R420, R421, R422, R423: SHORT_SMD_0805
SENSOR1: MAXTEC_Max-12c; TERMINAL_PIN_3_2.54mm

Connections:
3.3V: C2.2, C3.2, C4.2, C5.2, C6.2, C7.2, C8.2, C9.2, C10.2, C11.2, C12.2, C13.2, C14.1, C20.1, C21.1, C35.1, C38.1, C39.1, C43.2, C44.2, IC1.24, IC2.24, IC4.8, PRESS1.2, PRESS2.2, PRESS3.2, PRESS4.2, PRESS5.2, PRESS6.2, PRESS7.2, PRESS8.2, PRESS9.2, PRESS10.2, PRESS11.2, PRESS12.2, PRESS13.2, R13.2, R17.2, R35.1, R37.1, R156.2, R158.2, R160.2, R162.2, R170.2, R172.2, R176.2, R178.2, R233.2, R234.1, R235.1, R238.1, R239.1, R240.1, R241.1, R244.1, R245.1, R246.1, R247.1, R249.1, R250.2, R251.1, R252.2, R253.1, R254.2, R255.1, R256.2, R260.1, R261.2, R262.1, R263.2, R264.2, R265.1, R266.2, R267.1, R268.2, R269.1, R270.2, R271.1, R272.2, R277.1, R278.2, R279.1, R280.2, R282.1, R283.2, R284.1, R285.2, R316.2, R318.2, R320.2, R322.2, R371.2, R403.2, R405.1, R426.1, R427.1, R428.1, R429.2, R430.2, R431.2
5V: C22.2, C36.1, C40.1, C41.1, C45.1, IC3.6, R32.1, R38.1, R53.1, R62.2, R112.2, R155.2, R157.2, R169.2, R171.2, R231.1, R281.1, R372.2, R376.2, R396.2, R421.2
12V: C37.1, C42.1, C46.1, C47.1, R39.1, R300.2, R301.2, R317.2, R319.2, R321.2, R323.2, R373.2, R404.1, R422.2, R423.2
ALARM1_HIGH: R118.1, R409.1
ALARM1_LOW: R1.2, R407.1
ALARM1_MED: R43.1, R408.1
ALARM2_CNTRL: R85.2, R378.2
BAT-CHARGE-EN: R47.1, R415.1
BAT-MEAS-ANALOG: R40.2, R412.1
BAT-MEAS-EN: R46.1, R414.1
BUZZ1_EN: R19.2, R375.2
CPU_UART_CLK: R68.2, R402.2
CPU_UART_CTS: R91.1, R401.2
CPU_UART_RTS: R90.1, R400.2
CPU_UART_RX: R70.2, R399.2
CPU_UART_TX: R67.2, R398.2
DRIVE1_CH1_EN: R61.1, R286.2
DRIVE1_CH2_EN: R60.1, R287.2
DRIVE1_CH3_EN: R94.1, R288.2
DRIVE1_CH4_EN: R58.1, R289.2
DRIVE1_CH5_EN: R59.1, R290.2
DRIVE1_CH6_EN: R86.1, R291.2
DRIVE1_CH7_EN: R15.1, R292.2
DRIVE2_CH1_EN: R100.1, R293.2
DRIVE2_CH2_EN: R101.1, R294.2
DRIVE2_CH3_EN: R42.1, R295.2
DRIVE2_CH4_EN: R87.1, R296.2
DRIVE2_CH5_EN: R57.1, R297.2
DRIVE2_CH6_EN: R54.1, R298.2
DRIVE2_CH7_EN: R95.1, R299.2
EXT_MEM_CS: R424.2, R428.2
EXT_MEM_HOLD: R427.2, R435.1
EXT_MEM_PROTECT: R426.2, R434.1
GND: BUZZ1.-, C1.2, C2.1, C3.1, C4.1, C5.1, C6.1, C7.1, C8.1, C9.1, C10.1, C11.1, C12.1, C13.1, C14.2, C15.2, C16.2, C17.2, C18.2, C19.2, C20.2, C21.2, C22.1, C24.2, C25.2, C26.2, C27.2, C28.2, C29.2, C30.2, C31.2, C32.2, C33.2, C34.2, C35.2, C36.2, C37.2, C38.2, C39.2, C40.2, C41.2, C42.2, C43.1, C44.1, C45.2, C46.2, C47.2, C48.2, C49.2, C50.2, C51.2, C52.2, C53.2, CONN1.4, CONN1.5, CONN1.6, CONN2.4, CONN2.5, CONN2.6, CONN3.4, CONN3.5, CONN3.6, CONN4.4, CONN4.5, CONN4.6, CONN5.2, CONN5.3, CONN5.4, CONN6.2, CONN6.3, CONN6.4, CONN7.2, CONN7.3, CONN7.4, CONN8.2, CONN8.3, CONN8.4, CONN9.2, CONN9.3, CONN9.4, CONN10.2, CONN10.3, CONN10.4, CONN11.2, CONN11.3, CONN11.4, CONN12.2, CONN12.3, CONN12.4, CONN13.2, CONN13.3, CONN13.4, CONN14.2, CONN14.3, CONN14.4, CONN15.2, CONN15.3, CONN15.4, CONN16.2, CONN16.3, CONN16.4, CONN17.2, CONN17.3, CONN17.4, CONN18.2, CONN18.3, CONN18.4, CONN19.5, CONN19.6, CONN20.5, CONN20.6, CONN21.5, CONN21.6, CONN22.5, CONN22.6, DRIVE1.8, DRIVE2.8, DRIVE3.1, DRIVE3.7, DRIVE4.1, DRIVE4.7, DRIVE5.1, DRIVE5.7, DRIVE6.1, DRIVE6.7, H1.P1, H2.P1, H3.P1, H4.P1, H5.P1, H6.P1, IC1.12, IC2.12, IC3.1, IC3.7, IC3.15, IC4.4, PRESS1.1, PRESS2.1, PRESS3.1, PRESS4.1, PRESS5.1, PRESS6.1, PRESS7.1, PRESS8.1, PRESS9.1, PRESS10.1, PRESS11.1, PRESS12.1, PRESS13.3, PRESS14.2, PRESS14.9, PRESS14.10, PRESS15.2, PRESS15.9, PRESS15.10, PRESS16.2, PRESS16.5, PRESS16.6, PRESS17.2, PRESS17.9, PRESS17.10, PRESS18.2, PRESS18.9, PRESS18.10, Q1.2, R6.2, R14.2, R20.2, R33.1, R34.2, R36.1, R63.2, R96.1, R113.2, R114.2, R173.2, R174.2, R201.2, R202.2, R204.2, R205.2, R207.2, R208.2, R211.1, R222.1, R237.1, R274.1, R344.1, R345.1, R351.1, R352.1, R358.1, R359.1, R365.1, R366.1, R368.2, R369.2, R370.2, R374.2, R377.2, R384.2, R385.2, R395.2, R397.2, R413.1, R420.2
GPIO1: R88.1, R392.2
GPIO2: R97.1, R393.2
GPIO3: R98.1, R394.2
I2C1_RESET: R110.1, R203.2, R234.2
I2C1_SC0: R163.2, R186.1, R245.2
I2C1_SC1: R180.2, R188.1, R250.1
I2C1_SC2: R166.2, R190.1, R254.1
I2C1_SC3: R182.2, R192.1, R261.1
I2C1_SC4: R168.2, R218.1, R266.1
I2C1_SC5: R184.2, R216.1, R270.1
I2C1_SC6: CONN1.2, R214.1, R278.1
I2C1_SC7: CONN2.3, R212.1, R283.1
I2C1_SCL: R69.2, R210.1, R239.2
I2C1_SD0: R164.2, R185.1, R244.2
I2C1_SD1: R179.2, R187.1, R249.2
I2C1_SD2: R165.2, R189.1, R253.2
I2C1_SD3: R181.2, R191.1, R260.2
I2C1_SD4: R167.2, R219.1, R265.2
I2C1_SD5: R183.2, R217.1, R269.2
I2C1_SD6: CONN1.3, R215.1, R277.2
I2C1_SD7: CONN2.2, R213.1, R282.2
I2C1_SDA: R93.1, R209.1, R238.2
I2C2_RESET: R111.1, R206.2, R235.2
I2C2_SC0: R129.2, R194.1, R247.2
I2C2_SC1: R147.2, R196.1, R252.1
I2C2_SC2: R132.2, R198.1, R256.1
I2C2_SC3: R150.2, R200.1, R263.1
I2C2_SC4: R135.2, R229.1, R268.1
I2C2_SC5: R153.2, R227.1, R272.1
I2C2_SC6: CONN3.3, R225.1, R280.1
I2C2_SC7: CONN4.3, R223.1, R285.1
I2C2_SCL: R55.1, R221.1, R241.2
I2C2_SD0: R128.2, R193.1, R246.2
I2C2_SD1: R146.2, R195.1, R251.2
I2C2_SD2: R131.2, R197.1, R255.2
I2C2_SD3: R149.2, R199.1, R262.2
I2C2_SD4: R134.2, R230.1, R267.2
I2C2_SD5: R152.2, R228.1, R271.2
I2C2_SD6: CONN3.2, R226.1, R279.2
I2C2_SD7: CONN4.2, R224.1, R284.2
I2C2_SDA: R56.1, R220.1, R240.2
I2C3_SCL: R102.1, R242.2, R258.1
I2C3_SDA: R71.2, R243.2, R259.1
LED1_EN: D1.2, R49.1
LED2_EN: D2.2, R50.1
LED3_EN: D3.2, R51.1
LEDB_EN: R9.1, R380.2
LEDG_EN: R10.1, R381.2
LEDR_EN: R8.1, R379.2
LTC4421-PWR-nCH1: R30.2, R419.1
LTC4421-PWR-nCH2: R41.2, R418.1
LTC4421-PWR-nDISABLE1: R24.2, R388.2
LTC4421-PWR-nDISABLE2: R25.2, R389.2
LTC4421-PWR-nFAULT1: R27.2, R390.2
LTC4421-PWR-nFAULT2: R28.2, R391.2
LTC4421-PWR-nVALID1: R22.2, R387.2
LTC4421-PWR-nVALID2: R23.2, R386.2
MOTOR1_DIR: R72.2, R340.1
MOTOR1_EN: R83.2, R346.1
MOTOR1_STEP: R73.2, R341.1
MOTOR1_UART: R29.2, R342.1, R343.1
MOTOR2_DIR: R75.2, R354.1
MOTOR2_EN: R74.2, R360.1
MOTOR2_STEP: R76.2, R355.1
MOTOR2_UART: R16.2, R356.1, R357.1
MOTOR3_DIR: R78.2, R347.1
MOTOR3_EN: R77.2, R353.1
MOTOR3_STEP: R79.2, R348.1
MOTOR3_UART: R18.2, R349.1, R350.1
MOTOR4_DIR: R81.2, R361.1
MOTOR4_EN: R80.2, R367.1
MOTOR4_STEP: R82.2, R362.1
MOTOR4_UART: R31.2, R363.1, R364.1
unnamed: BUZZ1.+, R375.1
unnamed: C1.1, MOD1.CN11_6, R53.2
unnamed: C15.1, PRESS14.3, R159.1, R160.1
unnamed: C16.1, PRESS15.3, R161.1, R162.1
unnamed: C18.1, PRESS17.3, R175.1, R176.1
unnamed: C19.1, PRESS18.3, R177.1, R178.1
unnamed: C23.1, IC3.10, R257.2
unnamed: C23.2, IC3.9, R257.1
unnamed: C24.1, R273.1, R274.2, R281.2
unnamed: C25.1, C51.1, DRIVE1.9, R300.1
unnamed: C26.1, C52.1, DRIVE2.9, R301.1
unnamed: C27.1, DRIVE3.2, R316.1
unnamed: C28.1, C48.1, DRIVE3.8, R317.1
unnamed: C29.1, DRIVE4.2, R318.1
unnamed: C30.1, C49.1, DRIVE4.8, R319.1
unnamed: C31.1, DRIVE5.2, R320.1
unnamed: C32.1, C50.1, DRIVE5.8, R321.1
unnamed: C33.1, DRIVE6.2, R322.1
unnamed: C34.1, C53.1, DRIVE6.8, R323.1
unnamed: CONN1.1, R155.1, R156.1
unnamed: CONN2.1, R157.1, R158.1
unnamed: CONN3.1, R169.1, R170.1
unnamed: CONN4.1, R171.1, R172.1
unnamed: CONN5.1, R302.1
unnamed: CONN6.1, R303.1
unnamed: CONN7.1, R304.1
unnamed: CONN8.1, R305.1
unnamed: CONN9.1, R306.1
unnamed: CONN10.1, R307.1
unnamed: CONN11.1, R308.1
unnamed: CONN12.1, R309.1
unnamed: CONN13.1, R310.1
unnamed: CONN14.1, R311.1
unnamed: CONN15.1, R312.1
unnamed: CONN16.1, R313.1
unnamed: CONN17.1, R314.1
unnamed: CONN18.1, R315.1
unnamed: CONN19.1, R324.2
unnamed: CONN19.2, R325.2
unnamed: CONN19.3, R326.2
unnamed: CONN19.4, R327.2
unnamed: CONN20.1, R328.2
unnamed: CONN20.2, R329.2
unnamed: CONN20.3, R330.2
unnamed: CONN20.4, R331.2
unnamed: CONN21.1, R332.2
unnamed: CONN21.2, R333.2
unnamed: CONN21.3, R334.2
unnamed: CONN21.4, R335.2
unnamed: CONN22.1, R336.2
unnamed: CONN22.2, R337.2
unnamed: CONN22.3, R338.2
unnamed: CONN22.4, R339.2
unnamed: CONN23.1, R376.1
unnamed: CONN23.2, R404.2
unnamed: CONN23.3, R377.1
unnamed: CONN23.4, R405.2
unnamed: CONN23.5, R378.1
unnamed: CONN23.6, R406.2
unnamed: CONN23.7, R379.1
unnamed: CONN23.8, R407.2
unnamed: CONN23.9, R380.1
unnamed: CONN23.10, R408.2
unnamed: CONN23.11, R381.1
unnamed: CONN23.12, R409.2
unnamed: CONN23.13, R382.1
unnamed: CONN23.14, R410.2
unnamed: CONN23.15, R383.1
unnamed: CONN23.16, R411.2
unnamed: CONN24.1, R384.1
unnamed: CONN24.2, R412.2
unnamed: CONN24.3, R385.1
unnamed: CONN24.4, R413.2
unnamed: CONN24.5, R386.1
unnamed: CONN24.6, R414.2
unnamed: CONN24.7, R387.1
unnamed: CONN24.8, R415.2
unnamed: CONN24.9, R388.1
unnamed: CONN24.10, R416.2
unnamed: CONN24.11, R389.1
unnamed: CONN24.12, R417.2
unnamed: CONN24.13, R390.1
unnamed: CONN24.14, R418.2
unnamed: CONN24.15, R391.1
unnamed: CONN24.16, R419.2
unnamed: D1.1, R368.1
unnamed: D2.1, R369.1
unnamed: D3.1, R374.1
unnamed: DRIVE1.1, R286.1
unnamed: DRIVE1.2, R287.1
unnamed: DRIVE1.3, R288.1
unnamed: DRIVE1.4, R289.1
unnamed: DRIVE1.5, R290.1
unnamed: DRIVE1.6, R291.1
unnamed: DRIVE1.7, R292.1
unnamed: DRIVE1.10, R308.2
unnamed: DRIVE1.11, R307.2
unnamed: DRIVE1.12, R306.2
unnamed: DRIVE1.13, R305.2
unnamed: DRIVE1.14, R304.2
unnamed: DRIVE1.15, R303.2
unnamed: DRIVE1.16, R302.2
unnamed: DRIVE2.1, R293.1
unnamed: DRIVE2.2, R294.1
unnamed: DRIVE2.3, R295.1
unnamed: DRIVE2.4, R296.1
unnamed: DRIVE2.5, R297.1
unnamed: DRIVE2.6, R298.1
unnamed: DRIVE2.7, R299.1
unnamed: DRIVE2.10, R315.2
unnamed: DRIVE2.11, R314.2
unnamed: DRIVE2.12, R313.2
unnamed: DRIVE2.13, R312.2
unnamed: DRIVE2.14, R311.2
unnamed: DRIVE2.15, R310.2
unnamed: DRIVE2.16, R309.2
unnamed: DRIVE3.3, R324.1
unnamed: DRIVE3.4, R325.1
unnamed: DRIVE3.5, R326.1
unnamed: DRIVE3.6, R327.1
unnamed: DRIVE3.9, R340.2
unnamed: DRIVE3.10, R341.2
unnamed: DRIVE3.11, R342.2
unnamed: DRIVE3.12, R343.2
unnamed: DRIVE3.14, R344.2
unnamed: DRIVE3.15, R345.2
unnamed: DRIVE3.16, R346.2
unnamed: DRIVE4.3, R328.1
unnamed: DRIVE4.4, R329.1
unnamed: DRIVE4.5, R330.1
unnamed: DRIVE4.6, R331.1
unnamed: DRIVE4.9, R347.2
unnamed: DRIVE4.10, R348.2
unnamed: DRIVE4.11, R349.2
unnamed: DRIVE4.12, R350.2
unnamed: DRIVE4.14, R351.2
unnamed: DRIVE4.15, R352.2
unnamed: DRIVE4.16, R353.2
unnamed: DRIVE5.3, R332.1
unnamed: DRIVE5.4, R333.1
unnamed: DRIVE5.5, R334.1
unnamed: DRIVE5.6, R335.1
unnamed: DRIVE5.9, R354.2
unnamed: DRIVE5.10, R355.2
unnamed: DRIVE5.11, R356.2
unnamed: DRIVE5.12, R357.2
unnamed: DRIVE5.14, R358.2
unnamed: DRIVE5.15, R359.2
unnamed: DRIVE5.16, R360.2
unnamed: DRIVE6.3, R336.1
unnamed: DRIVE6.4, R337.1
unnamed: DRIVE6.5, R338.1
unnamed: DRIVE6.6, R339.1
unnamed: DRIVE6.9, R361.2
unnamed: DRIVE6.10, R362.2
unnamed: DRIVE6.11, R363.2
unnamed: DRIVE6.12, R364.2
unnamed: DRIVE6.14, R365.2
unnamed: DRIVE6.15, R366.2
unnamed: DRIVE6.16, R367.2
unnamed: IC1.1, R201.1
unnamed: IC1.2, R202.1
unnamed: IC1.3, R203.1
unnamed: IC1.4, R185.2
unnamed: IC1.5, R186.2
unnamed: IC1.6, R187.2
unnamed: IC1.7, R188.2
unnamed: IC1.8, R189.2
unnamed: IC1.9, R190.2
unnamed: IC1.10, R191.2
unnamed: IC1.11, R192.2
unnamed: IC1.13, R219.2
unnamed: IC1.14, R218.2
unnamed: IC1.15, R217.2
unnamed: IC1.16, R216.2
unnamed: IC1.17, R215.2
unnamed: IC1.18, R214.2
unnamed: IC1.19, R213.2
unnamed: IC1.20, R212.2
unnamed: IC1.21, R211.2
unnamed: IC1.22, R210.2
unnamed: IC1.23, R209.2
unnamed: IC2.1, R204.1
unnamed: IC2.2, R205.1
unnamed: IC2.3, R206.1
unnamed: IC2.4, R193.2
unnamed: IC2.5, R194.2
unnamed: IC2.6, R195.2
unnamed: IC2.7, R196.2
unnamed: IC2.8, R197.2
unnamed: IC2.9, R198.2
unnamed: IC2.10, R199.2
unnamed: IC2.11, R200.2
unnamed: IC2.13, R230.2
unnamed: IC2.14, R229.2
unnamed: IC2.15, R228.2
unnamed: IC2.16, R227.2
unnamed: IC2.17, R226.2
unnamed: IC2.18, R225.2
unnamed: IC2.19, R224.2
unnamed: IC2.20, R223.2
unnamed: IC2.21, R222.2
unnamed: IC2.22, R221.2
unnamed: IC2.23, R220.2
unnamed: IC3.3, R242.1
unnamed: IC3.4, R243.1
unnamed: IC3.11, R273.2
unnamed: IC3.12, R276.1, SENSOR1.3
unnamed: IC3.13, R275.1, R276.2, SENSOR1.2
unnamed: IC3.14, R275.2, SENSOR1.1
unnamed: IC4.1, R424.1
unnamed: IC4.2, R433.2
unnamed: IC4.3, R434.2
unnamed: IC4.5, R432.2
unnamed: IC4.6, R425.1
unnamed: IC4.7, R435.2
unnamed: J1.1, R370.1
unnamed: J1.2, R371.1
unnamed: J1.3, R372.1
unnamed: J1.4, R373.1
unnamed: J2.1, R392.1
unnamed: J2.2, R393.1
unnamed: J2.3, R394.1
unnamed: J2.4, R395.1
unnamed: J3.1, R396.1
unnamed: J3.2, R397.1
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

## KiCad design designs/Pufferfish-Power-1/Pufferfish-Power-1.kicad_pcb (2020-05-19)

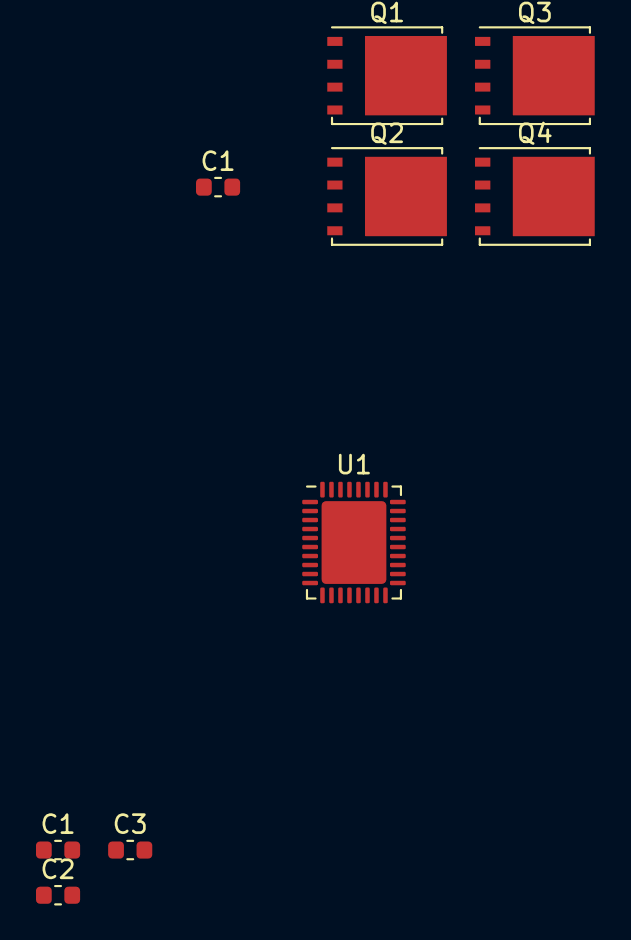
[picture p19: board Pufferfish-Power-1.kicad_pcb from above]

Board: 2 copper layers, 9 parts (0 on the bottom side), 7 nets, no tracks yet.

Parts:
C1, C1#2: CAP_1uF_35V_X7R_0603; CAP_SMD_0603
C2: CAP_1nF_50V_C0G_0402; CAP_SMD_0603
C3: CAP_100pF_10V_NP0_0402; CAP_SMD_0603
Q1, Q2, Q3, Q4: BSC028N06LS3; TDSON-8-1
U1: LTC4421IUHE; QFN-36-1EP_5x6mm_P0.5mm_EP3.6x4.6mm

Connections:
/LTC4221/LTC4421-QUAL: C2.1, U1.15
GND: C1.2, C1#2.2, C2.2, C3.2, U1.31, U1.37
INTVCC-LTC4421: C1.1, C1#2.1, C3.1, U1.12, U1.13
unnamed: Q1.1, Q1.2, Q1.3
unnamed: Q2.1, Q2.2, Q2.3
unnamed: Q3.1, Q3.2, Q3.3
unnamed: Q4.1, Q4.2, Q4.3

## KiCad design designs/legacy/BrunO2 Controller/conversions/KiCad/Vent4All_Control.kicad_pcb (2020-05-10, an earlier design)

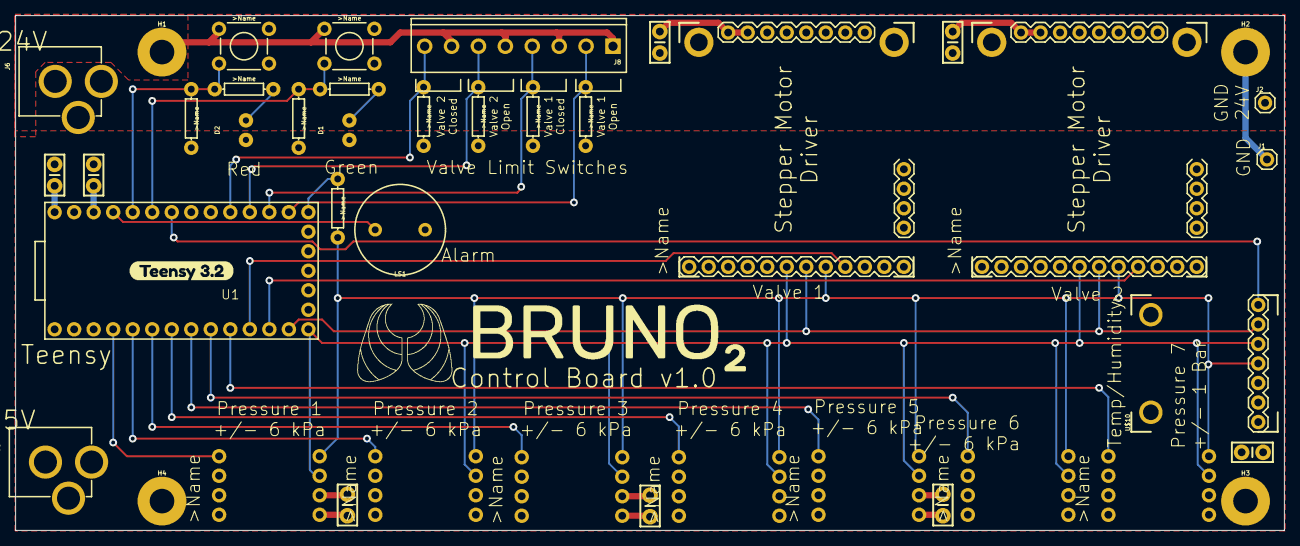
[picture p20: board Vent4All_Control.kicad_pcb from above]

Board: 2 copper layers, 165.1 x 67.0 mm, 43 parts (0 on the bottom side), 28 nets.

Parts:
C1, C2, C5, C6, C7, C8: 0.1uF; CAP-PTH-SMALL-KIT
C3, C4: 0.1uF 50V; CAP-PTH-SMALL-KIT
D1: GREEN; LED_5MM-KIT-NO-SILK
D2: RED; LED_5MM-KIT-NO-SILK
H1, H2, H3, H4: STANDOFF_ELECTRICAL-NOTHERMALS; STANDOFF-ELECTRICAL-NOTHERMALS
J1, J2: CONN_01; 1X01
J3, J6: POWER_JACK; POWER_JACK_PTH
J8: CONN-8-3.5MM_SCREW; SCREWTERMINAL-3.5MM-8
LS1: BUZZER-PTH; BUZZER-12MM
R1, R2: 470; AXIAL-0.3
R3, R4, R5, R6, R7, R8: 4.7k; AXIAL-0.3
R9: 25; AXIAL-0.3
S1, S2: MOMENTARY-SWITCH-SPST-PTH-6.0MM; TACTILE_SWITCH_PTH_6.0MM
U1: TEENSY-3.2PTH; TEENSY_TEENSY-3.2-PTH
U$1, U$2: POLOLU_36V4-MOUNTED; POLOLU_36V4
U$3, U$4, U$5, U$6, U$7, U$8: HSC_PRESSURE_SPI-HSCMRRN060MDSA3; HSC_PRESSURE_DIP
U$9: HSC_PRESSURE_SPI-HSCDRRN001BDSA3; HSC_PRESSURE_DIP
U$10: ADAFRUIT_BME280-BREAKOUT; ADAFRUIT_BME280
U$11: LOGO-BRUNO2; BRUNO2_LOGO

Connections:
3.3V: C2.1, C5.1, C6.1, C7.1, C8.1, D1.A, D2.A, R3.P$2, R4.P$2, R5.P$2, R6.P$2, R7.P$2, R8.P$2, U1.3.3V, U1.3.3V-1, U$1.2, U$1.10, U$2.2, U$2.10, U$3.2, U$4.2, U$5.2, U$6.2, U$7.2, U$8.2, U$9.2, U$10.1
5V: C1.1, J3.PWR, U1.VIN
/BUZZER: LS1.+, U1.23
/CS_BME280: U1.20, U$10.7
/CS_M1: U1.9, U$1.9
/CS_M2: U1.10, U$2.9
/CS_PS1: U1.2, U$3.5
/CS_PS2: U1.3, U$4.5
/CS_PS3: U1.4, U$5.5
/CS_PS4: U1.5, U$6.5
/CS_PS5: U1.6, U$7.5
/CS_PS6: U1.7, U$8.5
/CS_PS7: U1.8, U$9.5
/GND_24: C3.2, C4.2, J2.1, J6.GND, J6.GNDBREAK, U$1.21, U$1.22, U$1.MOUNT_1, U$1.MOUNT_2, U$2.21, U$2.22, U$2.MOUNT_1, U$2.MOUNT_2
/LED_GREEN: R1.P$1, R3.P$1, S1.3, U1.21
/LED_RED: R2.P$1, R4.P$1, S2.3, U1.22
/MISO: U1.12, U$1.6, U$2.6, U$3.3, U$4.3, U$5.3, U$6.3, U$7.3, U$8.3, U$9.3, U$10.5
/MOSI: U1.11, U$1.7, U$2.7, U$10.6
/SCK: R9.P$2, U$1.8, U$2.8, U$3.4, U$4.4, U$5.4, U$6.4, U$7.4, U$8.4, U$9.4, U$10.4
/VALVE1_C: J8.4, R6.P$1, U1.15
/VALVE1_O: J8.2, R5.P$1, U1.14
/VALVE2_C: J8.8, R8.P$1, U1.17
/VALVE2_O: J8.6, R7.P$1, U1.16
GND: C1.2, C2.2, C5.2, C6.2, C7.2, C8.2, H1.P1, H2.P1, H3.P1, H4.P1, J1.1, J3.GND, J3.GNDBREAK, J8.1, J8.3, J8.5, J8.7, LS1.-, S1.1, S2.1, U1.AGND, U1.GND, U1.GND1, U$1.3, U$2.3, U$3.1, U$4.1, U$5.1, U$6.1, U$7.1, U$8.1, U$9.1, U$10.3
unnamed: D1.K, R1.P$2
unnamed: D2.K, R2.P$2
unnamed: R9.P$1, U1.13
VIN: C3.1, C4.1, J6.PWR, U$1.23, U$1.24, U$2.23, U$2.24

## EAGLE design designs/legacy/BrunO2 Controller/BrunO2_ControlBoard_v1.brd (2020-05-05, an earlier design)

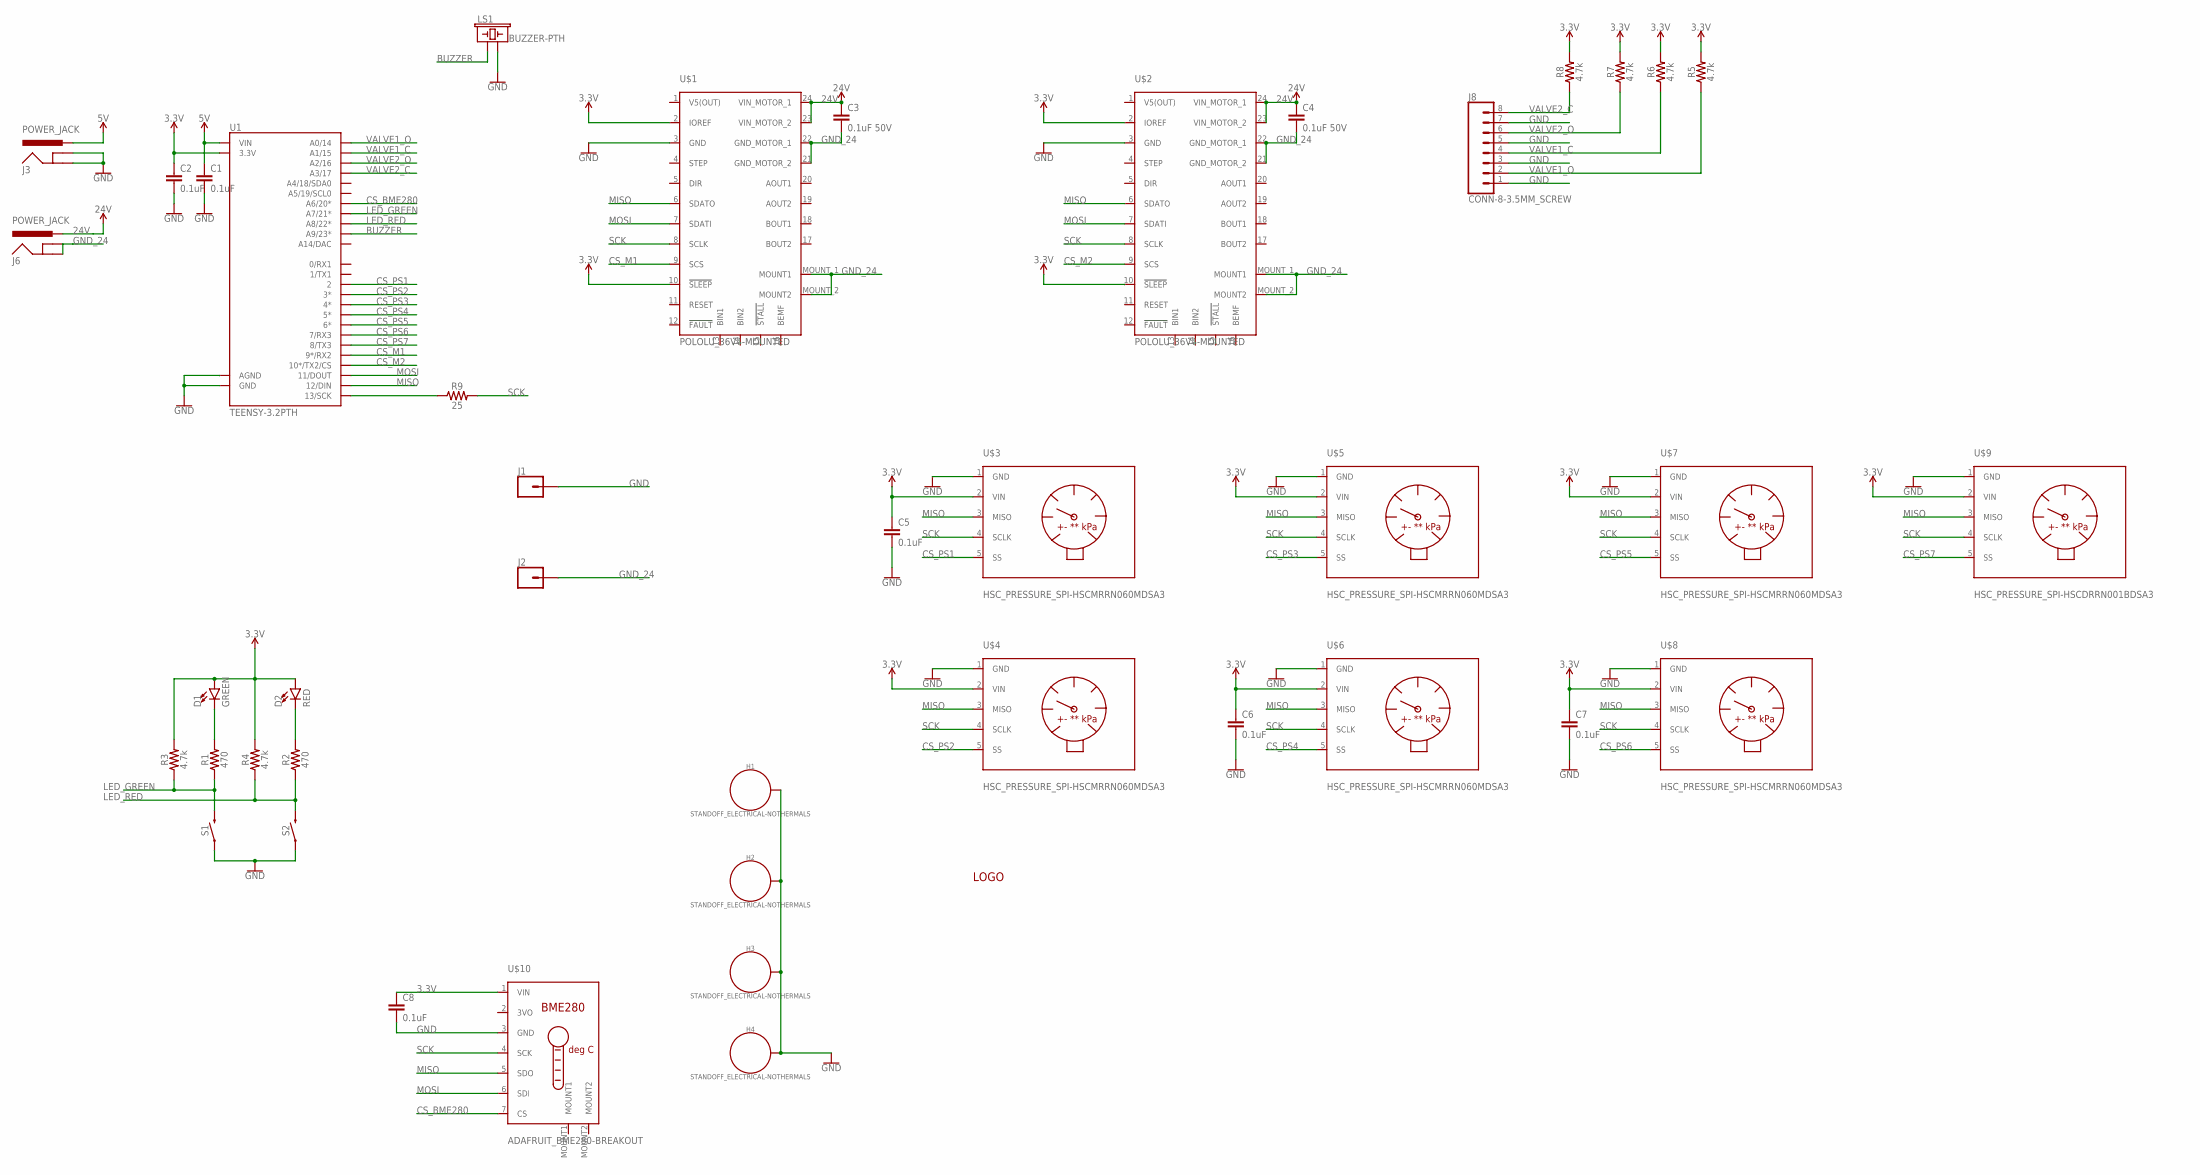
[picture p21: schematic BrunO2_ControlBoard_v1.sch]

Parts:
C1, C2, C5, C6, C7, C8: 0.1uF; CAP-PTH-SMALL-KIT
C3, C4: 0.1uF 50V; CAP-PTH-SMALL-KIT
D1: GREEN; LED_5MM-KIT-NO-SILK
D2: RED; LED_5MM-KIT-NO-SILK
H1, H2, H3, H4: STANDOFF_ELECTRICAL-NOTHERMALS; STANDOFF-ELECTRICAL-NOTHERMALS
J1, J2: CONN_01; 1X01
J3, J6: POWER_JACK; POWER_JACK_PTH
J8: CONN-8-3.5MM_SCREW; SCREWTERMINAL-3.5MM-8
LS1: BUZZER-PTH; BUZZER-12MM
R1, R2: 470; AXIAL-0.3
R3, R4, R5, R6, R7, R8: 4.7k; AXIAL-0.3
R9: 25; AXIAL-0.3
S1, S2: MOMENTARY-SWITCH-SPST-PTH-6.0MM; TACTILE_SWITCH_PTH_6.0MM
U1: TEENSY-3.2PTH; TEENSY_TEENSY-3.2-PTH
U$1, U$2: POLOLU_36V4-MOUNTED; POLOLU_36V4
U$3, U$4, U$5, U$6, U$7, U$8: HSC_PRESSURE_SPI-HSCMRRN060MDSA3; HSC_PRESSURE_DIP
U$9: HSC_PRESSURE_SPI-HSCDRRN001BDSA3; HSC_PRESSURE_DIP
U$10: ADAFRUIT_BME280-BREAKOUT; ADAFRUIT_BME280
U$11: LOGO-BRUNO2; BRUNO2_LOGO

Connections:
3.3V: C2.1, C5.1, C6.1, C7.1, C8.1, D1.A, D2.A, R3.P$2 (2), R4.P$2 (2), R5.P$2 (2), R6.P$2 (2), R7.P$2 (2), R8.P$2 (2), U1.3.3V, U1.3.3V-1 (3.3V), U$1.2 (IOREF), U$1.10 (!SLEEP), U$2.2 (IOREF), U$2.10 (!SLEEP), U$3.2 (VIN), U$4.2 (VIN), U$5.2 (VIN), U$6.2 (VIN), U$7.2 (VIN), U$8.2 (VIN), U$9.2 (VIN), U$10.1 (VIN)
5V: C1.1, J3.PWR, U1.VIN
24V: C3.1, C4.1, J6.PWR, U$1.23 (VIN_MOTOR_2), U$1.24 (VIN_MOTOR_1), U$2.23 (VIN_MOTOR_2), U$2.24 (VIN_MOTOR_1)
BUZZER: LS1.+ (1), U1.23 (A9/23*)
CS_BME280: U1.20 (A6/20*), U$10.7 (CS)
CS_M1: U1.9 (9*/RX2), U$1.9 (SCS)
CS_M2: U1.10 (10*/TX2/CS), U$2.9 (SCS)
CS_PS1: U1.2, U$3.5 (SS)
CS_PS2: U1.3 (3*), U$4.5 (SS)
CS_PS3: U1.4 (4*), U$5.5 (SS)
CS_PS4: U1.5 (5*), U$6.5 (SS)
CS_PS5: U1.6 (6*), U$7.5 (SS)
CS_PS6: U1.7 (7/RX3), U$8.5 (SS)
CS_PS7: U1.8 (8/TX3), U$9.5 (SS)
GND: C1.2, C2.2, C5.2, C6.2, C7.2, C8.2, H1.P1, H2.P1, H3.P1, H4.P1, J1.1, J3.GND, J3.GNDBREAK, J8.1, J8.3, J8.5, J8.7, LS1.- (2), S1.1, S2.1, U1.AGND, U1.GND, U1.GND1 (GND), U$1.3 (GND), U$2.3 (GND), U$3.1 (GND), U$4.1 (GND), U$5.1 (GND), U$6.1 (GND), U$7.1 (GND), U$8.1 (GND), U$9.1 (GND), U$10.3 (GND)
GND_24: C3.2, C4.2, J2.1, J6.GND, J6.GNDBREAK, U$1.21 (GND_MOTOR_2), U$1.22 (GND_MOTOR_1), U$1.MOUNT_1 (MOUNT1), U$1.MOUNT_2 (MOUNT2), U$2.21 (GND_MOTOR_2), U$2.22 (GND_MOTOR_1), U$2.MOUNT_1 (MOUNT1), U$2.MOUNT_2 (MOUNT2)
LED_GREEN: R1.P$1 (1), R3.P$1 (1), S1.3 (2), U1.21 (A7/21*)
LED_RED: R2.P$1 (1), R4.P$1 (1), S2.3 (2), U1.22 (A8/22*)
MISO: U1.12 (12/DIN), U$1.6 (SDATO), U$2.6 (SDATO), U$3.3 (MISO), U$4.3 (MISO), U$5.3 (MISO), U$6.3 (MISO), U$7.3 (MISO), U$8.3 (MISO), U$9.3 (MISO), U$10.5 (SDO)
MOSI: U1.11 (11/DOUT), U$1.7 (SDATI), U$2.7 (SDATI), U$10.6 (SDI)
unnamed: D1.K (C), R1.P$2 (2)
unnamed: R9.P$1 (1), U1.13 (13/SCK)
unnamed: D2.K (C), R2.P$2 (2)
SCK: R9.P$2 (2), U$1.8 (SCLK), U$2.8 (SCLK), U$3.4 (SCLK), U$4.4 (SCLK), U$5.4 (SCLK), U$6.4 (SCLK), U$7.4 (SCLK), U$8.4 (SCLK), U$9.4 (SCLK), U$10.4 (SCK)
VALVE1_C: J8.4, R6.P$1 (1), U1.15 (A1/15)
VALVE1_O: J8.2, R5.P$1 (1), U1.14 (A0/14)
VALVE2_C: J8.8, R8.P$1 (1), U1.17 (A3/17)
VALVE2_O: J8.6, R7.P$1 (1), U1.16 (A2/16)

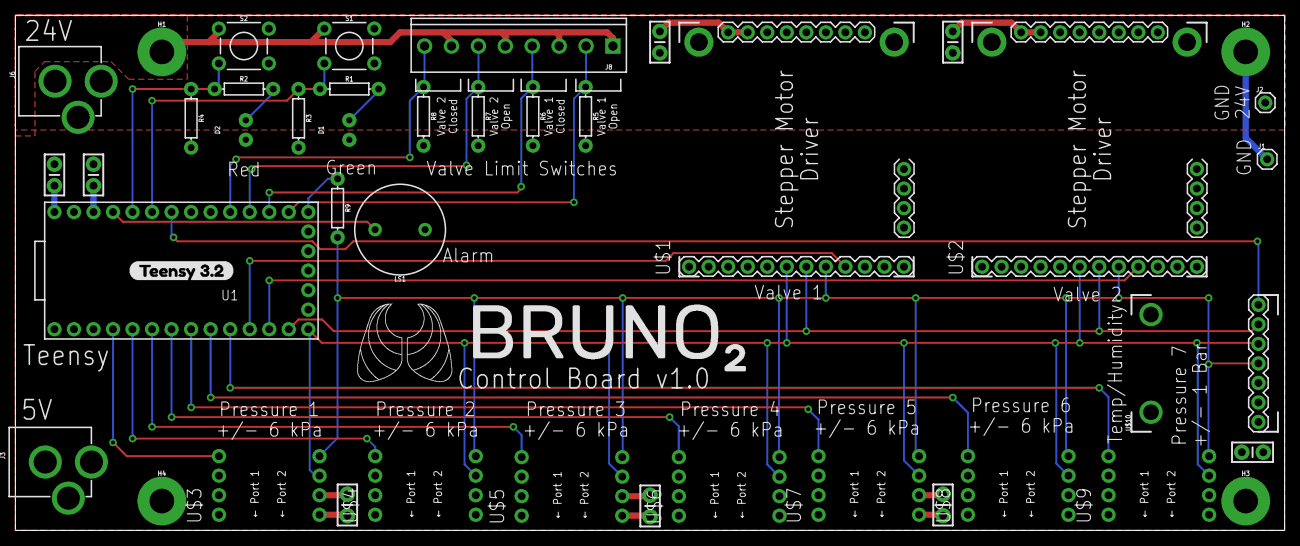
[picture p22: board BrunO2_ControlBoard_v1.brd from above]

Board: 2 copper layers, 165.1 x 67.0 mm, 43 parts (0 on the bottom side), 28 nets.

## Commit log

2020-05-05 adding the original PCB made by Marc for reference
    [BrunO2_ControlBoard_v1.brd, BrunO2_ControlBoard_v1.sch, copper_bottom.gbr, copper_top.gbr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]
2020-05-05 Added the Squid Motion Plane for reference.
    This design comes from the Octopi microscope project, which uses a stack of boards (connected by stacking headers) for different modules. This module is used for controlling stepper motors.
    [Motion Plane.pcbdoc, Motion Plane.schdoc, Pick and Place.csv]
2020-05-10 Initial Vent4All PCBA project upload: - Part libraries imported mostly from BrunO2_ControlBoard_v1 Eagle - Added HSC SMT pressure sensor - Imported Nucleo 144 CAD symbol and footprint - Prepared page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
    [Alarms.sch, Flow-sensors.sch, MCU-SymbolA.sch, MCU-SymbolB.sch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]
2020-05-11 Added global labels for reserved communication lines (SPI, I2C, UARTs).
    Added hierarchical sheet for external connection interfaces (e.g. to RPi).
    Changed symbol libraries table to use ${KIPRJMOD} instead of absolute paths.
    When I imported the schematic, KiCAD made a rescue library and changed the line endings of all the .sch files.
    [Alarms.sch, External.sch, Flow-sensors.sch, MCU-SymbolA.sch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]
2020-05-12 Added schematic connections for HSC sensors.
    Note: this assumes HSC sensors will be soldered directly to the PCB. If we are placing them on daughter boards then we will need to choose the pin header connectors and move the HSC symbols into a se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
    [Alarms.sch, External.sch, MCU-SymbolA.sch, Pressure-sensors.sch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]
2020-05-12 renamed folders
    [Alarms.sch, Flow-sensors.sch, MCU-SymbolA.sch, MCU-SymbolB.sch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]
2020-05-12 moved legacy boards into their own folder
    [BrunO2_ControlBoard_v1.brd, BrunO2_ControlBoard_v1.sch, Motion Plane.pcbdoc, Motion Plane.schdoc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]
2020-05-12 reorganized structure of pufferfish board directories
    [Alarms.sch, Flow-sensors.sch, MCU-SymbolA.sch, MCU-SymbolB.sch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]
2020-05-13 made new central project and cleaned up old files
    [Pufferfish.kicad_pcb, Pufferfish.sch]
2020-05-13 organizing designs (a)
    [Alarms.sch, Flow-sensors.sch, MCU-SymbolA.sch, MCU-SymbolB.sch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]
2020-05-13 organizing designs (b)
    [Alarms.sch, Flow-sensors.sch, MCU-SymbolA.sch, MCU-SymbolB.sch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]
2020-05-13 organizing designs (c)
    [Alarms.sch, BrunO2_ControlBoard_v1.brd, BrunO2_ControlBoard_v1.sch, Flow-sensors.sch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]
2020-05-13 organizing designs (d)
    [Actuators.sch, Microcontroller.sch, Peripheral.sch, Pufferfish-Controller-1.kicad_pcb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]
2020-05-13 removed migrated files
    [Alarms.sch, Flow-sensors.sch, MCU-SymbolA.sch, MCU-SymbolB.sch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]
2020-05-13 initialized controller schematics
    [Connectors.sch, Microcontroller.sch, Peripheral.sch, Pufferfish-Controller-1.kicad_pcb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]
2020-05-14 added pressure sensors
    [Microcontroller.sch, Sensors.sch]
2020-05-14 started adding peripherals
    [Actuators.sch, Connectors.sch, Microcontroller.sch, Peripheral.sch]
2020-05-14 added passives to library
    [Connectors.sch, Microcontroller.sch, Peripheral.sch, Sensors.sch]
2020-05-14 part library updates
    [Peripheral.sch, Sensors.sch]
2020-05-15 added todos
    [Actuators.sch, Connectors.sch, Microcontroller.sch, Peripheral.sch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]
2020-05-18 - Added Pufferfish logo to KiCad template - Started Power schematic - Added LTC4421 to library - Added a few capacitors to design - Added placeholder FETs (will select carefully soon)
    [LTC4221.sch, Pufferfish-Power-1.kicad_pcb, Pufferfish-Power-1.sch]
2020-05-19 added motor drivers
    [Pufferfish.sch]
2020-05-19 updated controller schematics
    [Actuators.sch, Connectors.sch, Microcontroller.sch, Peripheral.sch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]
2020-05-19 Changed library and template directories to relative paths for portability
    [Pufferfish-Power-1.kicad_pcb]
2020-05-20 added the rest of the sensors and drivers
    [Actuators.sch, Connectors.sch, Microcontroller.sch, Sensors.sch]
2020-05-20 updated controller nets and added interface board project
    [Actuators.sch, Connectors.sch, Microcontroller.sch, Peripheral.sch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]
2020-05-20 updated oxygen sensor readout circuit
    [Connectors.sch, Sensors.sch]
2020-06-02 updated actuators, MCU connections, and headers
    [Actuators.sch, Connectors.sch, Microcontroller.sch, Peripheral.sch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]
2020-06-02 updates pin assignments and added CSV list of pin assignments
    [Microcontroller.sch, Pufferfish-Controller-1-Pins.csv, Sensors.sch]
2020-06-03 added ports and parts for I2C pressure sensors
    [Actuators.sch, Microcontroller.sch, Peripheral.sch, Pufferfish-Controller-1.kicad_pcb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]
2020-06-03 updated pin list
    [Pufferfish-Controller-1-Pins.csv]
2020-06-03 added I2C muxes and wired previous and new I2C pressure sensors to it
    [Microcontroller.sch, Peripheral.sch, Sensors.sch]
2020-06-03 added onboard power regulators and power jack
    [Actuators.sch, Microcontroller.sch, Peripheral.sch, Pufferfish-Controller-1.kicad_pcb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]
2020-06-03 updated pin assignment list
    [Actuators.sch, Microcontroller.sch, Peripheral.sch, Pufferfish-Controller-1-Pins.csv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]
2020-06-05 various updates since ENGN alignment meeting
    - removed the optional instrumentation amplifier
    - added the option to populate 5V instead of 3.3V for the EK-P4 sensors (so SFM3000 could be used instead)
    - provided a separate I2C line for the O2 sensor which max'es out its communication at 100kHz
    - changed MCU pins for the solenoid driver from GPIO to PWM
    [Drafting.sch, Microcontroller.sch, Sensors.sch]
2020-06-05 updated MCU pin assignment list
    [Pufferfish-Controller-1-Pins.csv]
2020-06-12 updated connectors and headers
    [Actuators.sch, Drafting.sch, Peripheral.sch, Pufferfish-Controller-1.sch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]
2020-06-12 provided software controlled 5V supply to SFM3000
    [Microcontroller.sch, Peripheral.sch, Sensors.sch]
2020-06-12 various pin and connector updates
    * updated flow sensor and terminal footprints to use JST plug in headers
    * allocated pins for MCU to power board communication (see pin assignments)
    * connected battery power supply measurement output to one of the MCUs ADC
    * updated the VIO for the TMC2209 motor driver modules from 5V to 3.3V
    [Actuators.sch, Microcontroller.sch, Peripheral.sch, Sensors.sch]
2020-06-15 added memory chip (migrated from interface board) and rounting to interface board
    [Peripheral.sch]
2020-06-15 updated pin assignment list, generated part references, added schematic PDF
    [Actuators.sch, Microcontroller.sch, Peripheral.sch, Pufferfish-Controller-1-Pins.csv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]
2020-06-17 added MCU connections to interface board connector and fixed power supply pin labels
    [Actuators.sch, Microcontroller.sch, Peripheral.sch, Pufferfish-Controller-1.kicad_pcb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]
2020-06-18 placed control components on PCB
    [Actuators.sch, Microcontroller.sch, Peripheral.sch, Pufferfish-Controller-1.kicad_pcb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]
2020-06-19 placed majority of components within target board size
    [Actuators.sch, Microcontroller.sch, Peripheral.sch, Pufferfish-Controller-1-Pins.csv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]
2020-06-22 finished component placement
    [Pufferfish-Controller-1.kicad_pcb]
2020-06-22 added ground and power planes
    [Pufferfish-Controller-1.kicad_pcb]
2020-06-23 autorouted traces using FreeRouting.jar
    [Pufferfish-Controller-1-freerouting.dsn, Pufferfish-Controller-1.dsn, Pufferfish-Controller-1.kicad_pcb]
2020-06-23 touched up routing and layed out power planes
    [Actuators.sch, Peripheral.sch, Pufferfish-Controller-1.kicad_pcb]
2020-06-23 completed PCB layout
    [Pufferfish-Controller-1.dsn, Pufferfish-Controller-1.kicad_pcb]
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2020-06-26 moved one of the unused GPIO pins from the jumper to the interface board connector
    [Peripheral.sch, Pufferfish-Controller-1.kicad_pcb]
2020-06-29 minor pcb updates and folder organization
    [Actuators.sch, Drafting.sch, Microcontroller.sch, Peripheral.sch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]
2020-06-29 generated Gerber files for submission to AdvancedCircuits
    [Pufferfish-Controller-1-B_Cu.gbr, Pufferfish-Controller-1-B_Mask.gbr, Pufferfish-Controller-1-B_Paste.gbr, Pufferfish-Controller-1-B_SilkS.gbr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]
2020-06-29 updated gerbers after correcting a DFM problem
    [Pufferfish-Controller-1-B_Cu.gbr, Pufferfish-Controller-1-B_Mask.gbr, Pufferfish-Controller-1-B_Paste.gbr, Pufferfish-Controller-1-B_SilkS.gbr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]
2020-06-29 moved around silkscreen labels and added BOM
    [Pufferfish-Controller-1-B_Cu.gbr, Pufferfish-Controller-1-B_Mask.gbr, Pufferfish-Controller-1-B_Paste.gbr, Pufferfish-Controller-1-B_SilkS.gbr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]
2020-06-30 added electrolytic capacitorss to drivers and regenerated fabrication files
    [Actuators.sch, Pufferfish-Controller-1-B_Cu.gbr, Pufferfish-Controller-1-B_Mask.gbr, Pufferfish-Controller-1-B_Paste.gbr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]
2020-06-30 updated BOM
    [Pufferfish-Controller-1-Materials.csv]
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2020-07-02 ensured all components point to the Pufferfish library and cleaned up the BOM
    [Microcontroller.sch, Pufferfish-Controller-1-Materials.csv, Pufferfish-Controller-1.kicad_pcb, Sensors.sch]
2020-07-02 cleaned up BOM
    [Pufferfish-Controller-1-Materials.csv]
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

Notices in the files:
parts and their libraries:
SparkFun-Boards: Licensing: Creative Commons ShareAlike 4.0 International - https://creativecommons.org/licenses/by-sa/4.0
